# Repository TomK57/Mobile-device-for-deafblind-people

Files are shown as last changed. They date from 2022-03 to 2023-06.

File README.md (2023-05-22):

# Mobile-device-for-deafblind-people
(Eine Beschreibung der Markdown Formatierung für die Datei findet sich [hier](https://github.com/adam-p/markdown-here/wiki/Markdown-Cheatsheet)
## Motivation
The biggest problem for deafblind people is social isolation.
Ofcourse they can read books printed in Braille or write a letter using a Braille keyboard, but this is not the same as talking with somebody.
## The aim of the project
is to provide a technical solution which allows deafblind people to talk with somebody as similar to a normal talk as possible. 
## The 5 bit code
 
## System requirements
The system shall allow for full duplex communication  
The system shall use the haptic capabilities of the human fingers  
There shall be one device to be used with one hand for sending the information  
There shall be a second device to be used with the other hand for receiving the information  
In buildings the communication link between devices shall use WLAN  
In the field the system shall use mobile  infrastructure like 4G and 5G.  
The devices shall use Bluetooth to connect to mobile phones as links to the mobile infrastructure      
Sender and receiver device shall be designed with best ergonomic properties in mind  
The sender device shall have 5 contacts, one for each finger  
The contacts shall provide haptic feedback when pressed  
The receiver device shall have 5 contacts, one for each finger  
The contacts shall provide a haptic feedback when an information is sent to that finger.  
The kind of haptic feedback shall allow for use over several quarters of an hour without leading to artifacts in the sensation of the fingers.   
## System architecture - Top Level
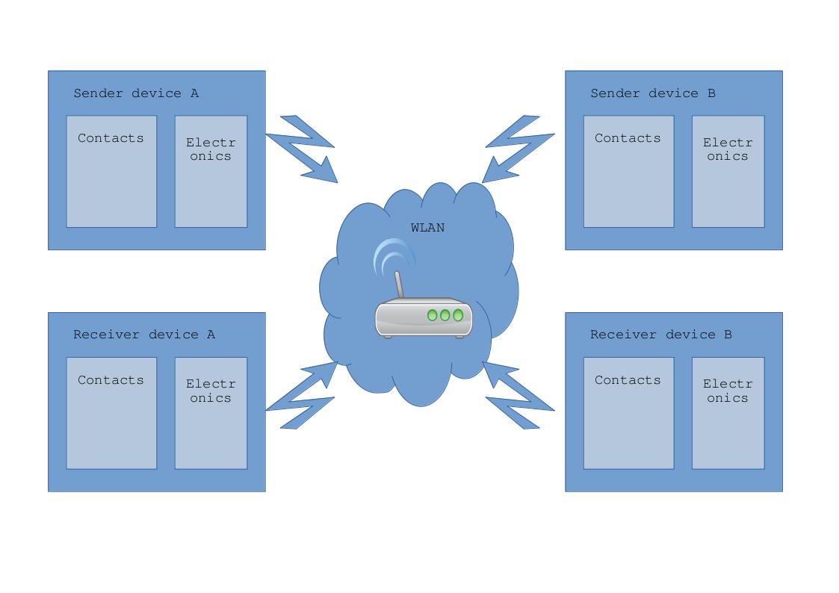
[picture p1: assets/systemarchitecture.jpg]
JPG image

### Power supply
The devices shall be able to operate from batteries (rechargeable).  
Battery lifetime tbd h (reasonable/acceptable)
### Performance
The devices shall be capable of processing at least 10 keystrokes per seconds   
## Pictures of some prototypes built so far
Evaluation of technical and ergonomic concepts<br><br>
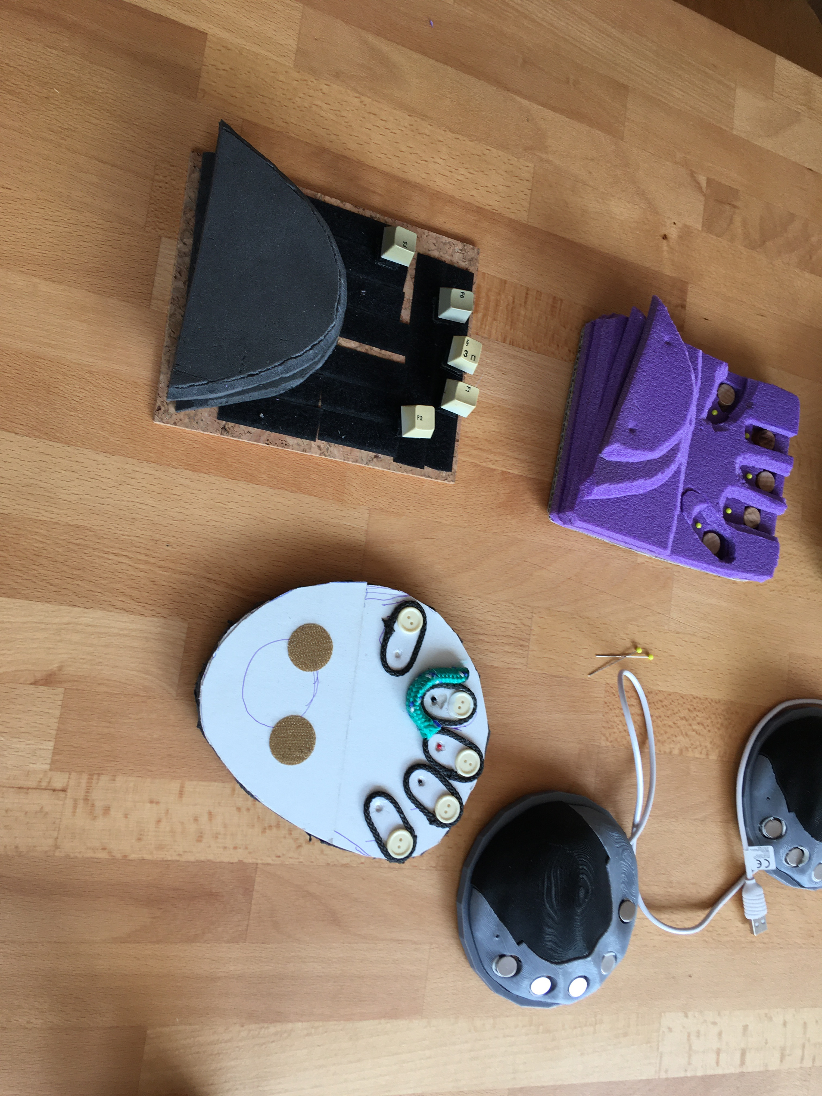
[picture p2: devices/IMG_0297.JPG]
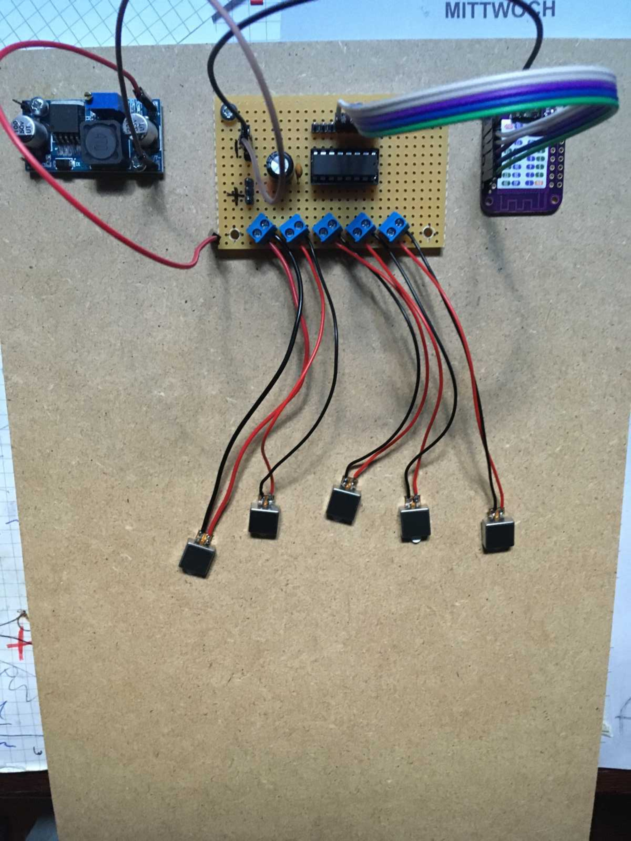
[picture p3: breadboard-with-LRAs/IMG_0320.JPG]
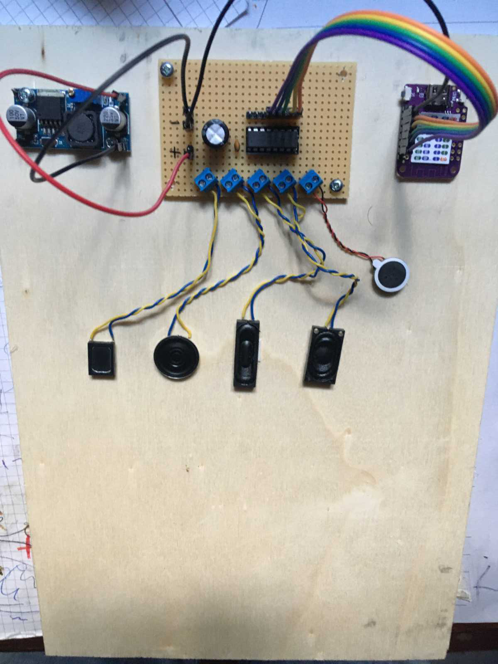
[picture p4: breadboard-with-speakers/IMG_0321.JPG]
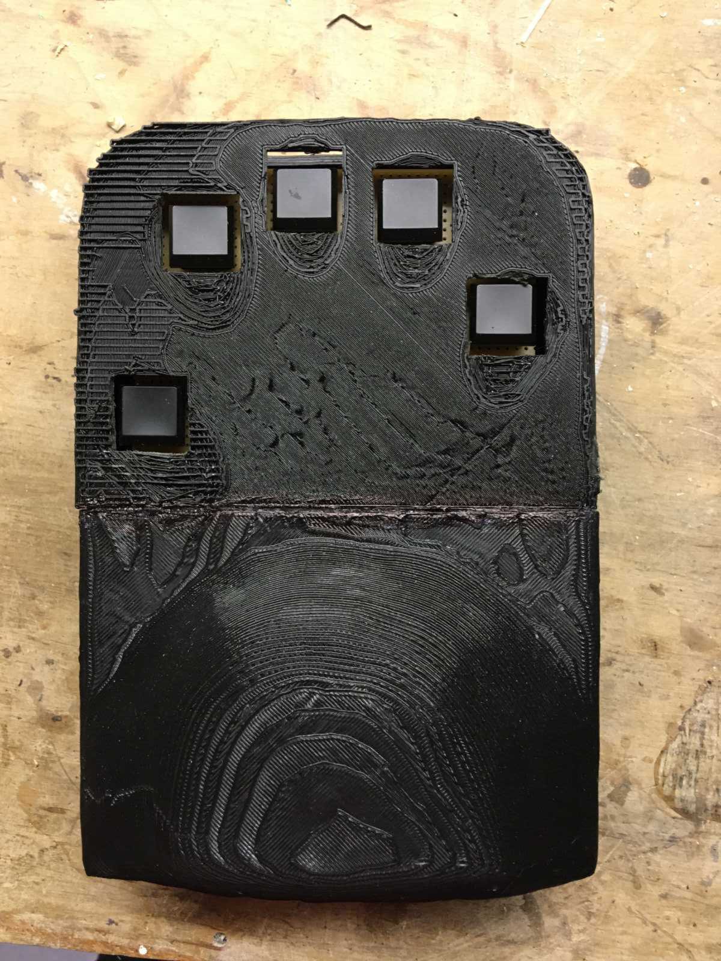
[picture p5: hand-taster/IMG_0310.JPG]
    <br>
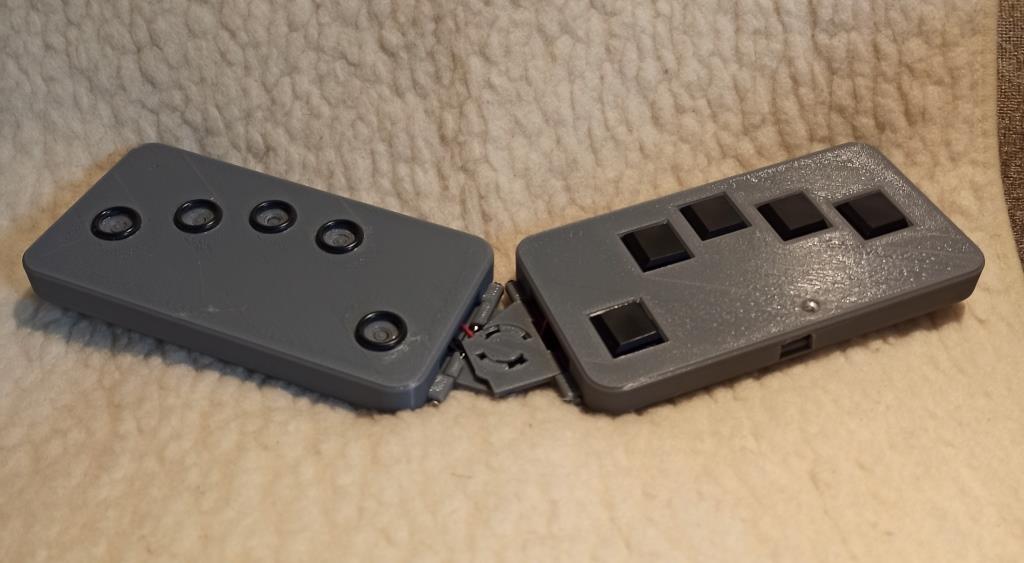
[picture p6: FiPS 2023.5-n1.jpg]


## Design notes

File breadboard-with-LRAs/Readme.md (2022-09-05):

## Breadboard with LRA's
LRAs are Loingitudinal Resonance Actuators, mostly used in mobiles. The model here is VLV101040A from vibronics.com.
This breadboard is used to test their usage for our purposes.
Electronics consist of WemosS2Mini controller, ULN2003 Darlington drver IC and a buck converter to provide the supply voltage for the LRAs independent from the controller.
The resonance frequecy of the LRA is 170Hz which means a period of about 5ms for one oscillation. We use only one half of this period to switch on voltage/current and let the device produce a mechanical pulse.
breadboard with LRAs
## software
to be used with hand taster device as input. ESP32_BLIND is basis for this modification.

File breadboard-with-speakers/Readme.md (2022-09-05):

## Breadboard with speakers
This device is intended to test the use of several speakers as actuators. Former tests showed that a user can feel the movement of the coil.
The electronics consist of Wemos S2 Mini (ESP32) controller, ULN2003 Darlington driver IC and a buck converter to provide the supply for the speakers indenpendent of the supply of the controller.
picture of breadboard
### Software
Works with the Handtaster device as input.

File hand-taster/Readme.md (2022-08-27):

## device for input with five low profile keys
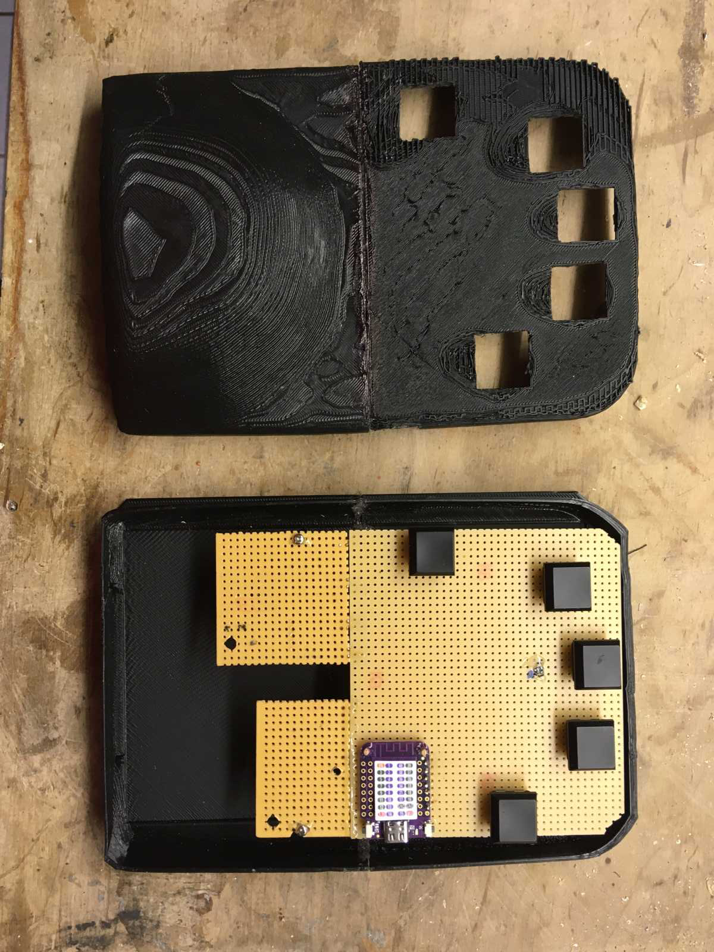
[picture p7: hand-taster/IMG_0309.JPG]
Bild1
<br>
Bild2<br>

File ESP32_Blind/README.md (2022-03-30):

DeafBlind Accesspoint / Websocket code with html webserver  for ESP32 or ESP8266                      copyright DHS, Desert Hard- & Software, Harald Wüst

See DB.docx Dokumentation...

Functionality:

The Sketch opens an acces point called "ap" with IP-adress 192.168.2.2.
A Web-Browser can access the startpage on this 192.168.2.2 or with http://dbserver.local

With the button "Socket communication" a socket connection to the device can be opened.

In the text field a single characters from the DeafBlind character set can be entered which is then send to the device and outputet to the DeafBlind tick-interface.

Also character entries made on the DeafBlind tick-interface are send to the web-socket console so that a communication with the DeafBlind can be established.

There are two special characters to extend the functionality:

- '#' This character switches to another character set (for example numbers, special characters). With each entry of a '#' character 
  the character set changes to the next one and back to the standard character set when the last set is reached (round robin).
  The following two character sets are currently available:
  'a','e','n','i','d','t','ä','o','k','m','f','l','g','ö','r','u','y','b','p','z','w','q','j','s','#','x','v','ü','c','h','*'  (standard set) and
  '1','2','3','4','5','6','7','8','9','0','!','"',' ','%','&','/','(',')','<','>',',','.','?',';','#','-','+',':','@','=','*'  (extended set)
  To destinguish the character sets on the DeafBlind tick-device for the first, normal set one pulse and for the second, third, ... sets two or more
  pulses are generated.
  After entering the next character from an extra character set the character set is automatically switched back to the standard character set.

- '*' This character switches to a special command mode. 
  In command mode the next entered character is interpreted as a special command:
  > '*' A second command character directly after the command character locks the comand mode permanently until another '*' character is recieved. This 
        can be used to enter a sequence of comands faster
  > 'w' Switch to local wifi network, the access point is closed and a connection to the local wifi network is established
  > 'c' Switch to client mode, the access point is colsed and a connection to another ap-server access point is opened to build up a network of devices.
  > 's' Switch to ap-server mode, the access point is opend to allow other devices to connect to the network of devices, only one server should be active.
  > 'n' Send new line/line feed character to begin a new input text line
  > 'm' Switch output mode, there are two output modes: 
        send all   -> sends every entered charcater including the special charcaters to all connected devices (standard mode after startup)
        send chars -> sends only the normal characters from the character set, special characters or commands are not send out 
        so that the output text is not disturbed
  > 'n' Send new line charater (cr/lf) to world
  > 'z' add space character ' ' to text line
  > 'e' Axecute previously stared text line (characters between the last new line commands. this can be used to process longer string comands also via
        tick-device (see description below). Example: * n s * z # 1 # 0 # 0 * n  command line "s 100" is stored, than * e to change stabTime
  > 'l' list alle connected devices with a given name to the world

All the single character input can come from the DeafBlind tick-device, the socket communication (other connected devices or web browsers) or the serial interface. So DeafBlind people can "talk" to each other or with non DeafBlinds using thier tick-devices.

If a longer string is entered via websocket or serial interface it is interpreted as a configuration command.
The first character of the command defines the functionality:

- 'o'   Send a string of characters to the network. Example "o hello" -> sends the character sequence  'h' 'e' 'l' 'l' 'o'  to the network 
        which is outputed to all connected DeafBlind tick devices.
- 's'   Set the stabilization time for character tick detection. Example s 20 -> sets the stabTime to 20 ms
- 'd'   Set the pulse duration for character tick output. Example d 20 -> sets the pulseDuration to 20 ms
- 'x'   Set the character speed for the 'o' command. Example x 200 -> sets the outSpeed to 200 ms
- 'n'   Change device name (wifi accesspoint and MDNS web browser name). Maximal length is 31 characters. Example n xy -> sets name to xy
- 'g'   Get (load) current configuration from file system. File ap.cfg is the startup configuration. Example g ap.cfg
- 'p'   Put (save) current configuration to file system. File ap.cfg is the startup configuration. File upload via web browser is possible. Example p ap.cfg
- 'i'   Change IP-Address, config save and reebot neccessary! (3.digit format with leading zerros) Example: i 192.168.002.002
- '!'   Special WebSocket command! Set name of connected device after new connection, to be send from client. Example: !xy -> sets device name to xy
- 'rrr' reeboot the tick-device

To start a DeafBlind network the devices should be startet one after the other giving them a uniqe name ('n MaxMusterman') and switch to client mode ('*' 'c'). Only the last device should stay in server mode where all other devices will than start to connect to.

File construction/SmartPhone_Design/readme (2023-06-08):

3D printing files for smartphone design Jun 2023

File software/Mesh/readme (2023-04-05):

DeafBlind SW for DeafBlind devices based on ESP32 S2 µC, PainlessMesh Mesh-Network and Arduino-IDE 2.01

Copyright Desert Hard- & Software dhs-web.de e-mail: dhs-mail.de

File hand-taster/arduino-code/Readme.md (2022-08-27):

## Arduino code for model with Wemos S2 mini controller

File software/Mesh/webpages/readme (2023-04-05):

Web-Pages for DeafBlind device

Copyright Desert Hard- und Software, dhs-web.de e-mail: dhs-mail@gmx.de

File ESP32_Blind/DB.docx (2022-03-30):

| DeafBlind Anleitung Software Version V0.5 ESP32 / ESP8266
| DHS Desert Hard- & Software Dr. Harald Wüst 30.03.2022

# DeafBlind Anleitung

Software Version V0.5 ESP32 / ESP8266

## 1. Aufbau eines Geräte-Netzwerks

Für ein Geräte-Netzwerk sind genau ein DeafBlind Server und mehrere Clients erforderlich.

Der DeafBlind Server stellt dazu einen WiFi Acces-Point mit dem Namen DBServer zur verfügung mit dem sich die Clients verbinden.

## 2. Tick Eingabe

Das Tick-Gerät dient der Eingabe einzelner Zeichen aus dem DeafBlind Zeichensatz sowie weiterer Befehle. Dazu müssen die Finger einer Hand die fünf Kontaktflächen des Gerätes im richtigen Muster berühren. Den Buchstaben ‚a‘ erhält man z.B. durch Berühren der ganz rechten Kontaktfläche (bei der rechten Hand unter dem Daumen). Für den Buchstaben ‚h‘ muss man die vier anderen Finger auf die jeweiligen Kontaktflächen legen. Dabei sollten die Finger möglichst gleichzeitig die Kontakte berühren (die Zeit bis zu der alle Finger in Position sein müssen kann eingestellt werden, siehe 1-Tick s-Befehl).

Eine solche Eingabe eines Zeichens wird im Folgenden als Tick bezeichnet.

Für die Eingabe weiterer Zeichen können die Finger entweder kurz vollständig abgehoben oder (bei gleichen Teilen des Musters) nur die zu ändernden Finger abgehoben bzw. aufgesetzt werden.

Die eingegebenen Zeichen werden an alle Teilnehmer des Netzwerkes gesendet und an allen Tick-Geräten als Vibration bzw. im Web-Browser oder dem seriellen Interface ausgegeben (wenn aktiviert wird das Zeichen auch auf dem eigenen Tick-Gerät als aktive Rückmeldung ausgegeben
Hinweis: Abschaltung aktuell noch nicht implementiert)

Die Kontaktflächen werden von links nach rechts im Weiteren so benannt:

D (aumen),
Z (eigefinger),
M (ittelfinger),
R (ingfinger),
K (leiner Finger)

Abgehobene Finger werden durch einen Striche -- gekennzeichnet.

Das Zeichen ‚h‘ vom obigen Beispiel entspricht damit dem Tick

-- Z M R K -> h

Werden alle Finger auf den Kontaktflächen aufgelegt wird kein Tick ausgelöst.

D Z M R K -> „zuhören“

Damit kann man der Unterhaltung „zuhören“ da alle Ticks der anderen Teilnehmer auf dem eigenen Tick-Gerät ausgegeben werden.

Hinweis: Da alle Eingaben direkt an alle Teilnehmer weiter gegeben werden kann es bei einer größeren Anzahl Teilnehmer schnell zu durcheinander kommen. Dies ist identisch mit dem durcheinander reden bei einer sprachlichen Unterhaltung und kann durch Disziplin der Teilnehmer reduziert werden.
Es kann auch auf den Rais-Hand Modus umgeschaltet werden in dem der DeafBlind Server die Rederechte verwaltet und immer nur ein Benutzer aktiv geschaltet ist. Die anderen Benutzer müssen zuerst das Rederecht durch ein „Handheben“ anfordern. Der Server fordert dann jeweils den nächsten Benutzer durch Ausgabe des Geräte-/Nutzer-Namens zum „reden“ auf.

Der RaiseHand Modus ist aktuell noch nicht vollständig Implementiert!

## 2.1. Zeichensätze

Der Standard-Zeichensatz ist folgender:

a D -- -- -- --
b -- Z -- -- K
c D – M R K
d D – M -- --
e -- Z -- -- --
f D Z -- -- --
g D – M R --
h -- Z M R K
i -- -- M -- --
j D Z M – K
k D -- -- R --
l -- -- M R --
m -- Z – R --
n D Z -- -- --
o -- -- -- R --
p D Z -- -- --
q -- Z M -- --
r D Z M R --
s -- -- -- R K
t -- Z M -- --
u -- -- -- -- K
v D Z -- R K
w D -- M -- K
x -- Z -- R K
y D -- -- -- K
z -- -- M – K
ä D Z M -- --
ö -- Z M R --

Über den speziellen Tick „Zeichensatzwechsel“ (im Weiteren als # bezeichnet):

# D -- -- R K

kann auf weitere Zeichensätze umgeschaltet werden:

1 2 3 4 5 6 7 8 …

A B C D E F G …

Dabei wird mit jedem Zeichensatzwechsel-Tick zwischen den Zeichensätzen im Kreis gewechselt. Da die Zeichenwechsel-Ticks ebenfalls an die anderen Teilnehmer übermittelt werden sind diese über den aktuell aktiven Zeichensatz informiert (abhängig vom Ausgabe-Modus, siehe m-Befehl).

Der neue Zeichensatz bleibt jeweils nur für das nächste Zeichen aktiv und wird dann wieder auf Normal zurück gesetzt.

Mit der Tick-Eingabe
# # h a l l o
bekommen Sie die Ausgabe
# # H a l l o
da durch zwei Mal # auf die Großbuchstaben umgeschaltet wurde.

Um die Umschaltung dauerhaft zu aktivieren (um z.B. eine längere Zahlenfolge einzugeben) muss nach der Wahl des Zeichensatzes der „Befehls-Zeichen“ Tick ‚*‘ gegeben werden (siehe Kap. 2):
# * a e n i
gibt die Ausgabe
# * 1 2 3 4

Mit dem nächsten Zeichensatz-Tick # wird wieder auf den Standard Zeichensatz zurück geschaltet.

Hinweis: Im Normal-Modus (siehe m-Befehl) kann eine zwischenzeitliche Tick-Eingabe eines anderen Teilnehmers die Umschaltung auf den dritten Zeichensatz und/oder die dauerhafte Aktivierung des Zeichensatzes stören (da dazu 2 direkt aufeinander folgende Ticks erforderlich sind).

## 3. 1-Tick Befehle

Mit dem speziellen Tick „Befehls-Zeichen“ (im Weiteren als * bezeichnet)

* -- -- M R K

können sogenannte 1-Tick Befehle ausgeführt werden. Damit lassen sich diverse Funktionen des Gerätes einfach steuern wobei die anderen Teilnehmer über alle Steuer-Befehle durch die Befehls-Zeichen Sequenz informiert sind (abhängig vom Ausgabe-Modus, siehe m-Befehl).

Ein 1-Tick Befehl besteht immer aus dem *-Tick gefolgt von dem gewünschten 1-Tick Befehlszeichen.

Hinweis: Im Normal-Modus (siehe m-Befehl) kann eine zwischenzeitliche Tick-Eingabe eines anderen Teilnehmers die Befehlsausführung stören oder zur Aktivierung eines falschen Befehls führen (da dazu 2 direkt aufeinander folgende Ticks erforderlich sind).

Eine mögliche Verbesserung durch Blockieren anderer Eingaben für eine gewisse Zeit und Rücknahme des Befehl-Ticks ist aktuell noch nicht umgesetzt!

Es gibt folgende 1-Tick Befehlszeichen / Funktionen:

## 3.1. w

Umschalten auf WLan Verbindung
Hinweis: aktuell feste Netzwerkdaten, Problem mit EEPROM-Lib auf ArduinoDroid!

## 3.2. c

Umschalten auf Client-Modus.
Es wird für 10 Sekunden versucht eine Verbindung zum DeafBlind Server (Access-Point DBServer) herzustellen und dem DeafBlind Netzwerk beizutreten. Wenn die Verbindung aufgebaut werden konnte wird der Name des Geräts/Benutzers an den Server übertragen (siehe n-Befehl). Andernfalls wird auf den Acces-Point Server Modus zurück geschaltet.

## 3.3. s

Umschalten auf Acces-Point Server Modus. Das Gerät stellt den DeafBlind-Server (DBServer) Access-Point zum Verbinden weitere Geräte im DeafBlind-Netzwerk zur Verfügung.

## 3.4. m

Ändern des Ausgabe-Modus. Im Standard Ausgabe-Modus (0) werden alle Zeichen incl. Befehlszeichen ausgegeben. Im Reduzierten Modus (1) werden die Befehlszeichen unterdrückt damit die Text-Ausgabe nicht gestört wird. Dieser Modus kann zum Schreiben von Texten benutzt werden.
Hinweis: Im reduzierten Modus sehen andere Teilnehmer die Befehlseingaben nicht und kennen daher Änderungen an der Systemkonfiguration nicht mehr.

Im Raise-Hand Modus (siehe r-Befehl) werden alle Ausgaben unterdrückt bis der Server die Raise-Hand Anfrage des Gerätes/Benutzers akzeptiert hat. Damit kann sicher gestellt werden, dass nicht mehrere Nutzer gleichzeitig kommunizieren.
Hinweis: Aktuell ist dieser Modus nicht vollständig implementiert.

## 3.5. r

Ein- / Ausschalten des Raise-Hand Modus.
Hinweis: Aktuell ist dieser Modus nicht vollständig implementiert.

## 3.6. h

Raise-Hand, Kommunikationsfreigabe beim Server anfordern

Hinweis: Aktuell ist dieser Modus nicht vollständig implementiert.

## 3.7. n

Sende „Return“ (Zeilenrücklauf / neue Zeile) an die verbundenen Geräte. Die seit dem letzten Zeilenwechsel gesendeten Zeichen werden in einem Zeilen-Speicher für die weitere Verwendung zwischengespeichert (siehe e-Befehl).

Es wird kein Zeichen an die Tick-Geräte gesende.

## 3.8. z

Sende „ “ (Leerzeichen) an die verbundenen Geräte. Das Leerzeichen wird nicht an den Tick-Geräte als Tick sondern nur als kurze Pause ausgegeben (siehe o-Befehl).

## 3.9. e

Ausführen einer gespeicherten Zeile (siehe n-Befehl). Über diese Funktion können auch Zeilen-Befehle (siehe Kap. 3) über ein Tick-Gerät ausgeführt werden indem zuerst eine neue leere Zeile über den n-Befehl gestartet wird, dann der gewünschte Zeilen-Befehl mit dem Tick-Gerät geschrieben und die Zeile mit einem weiteren n-Befehl abgeschlossen wird.

Der Zeilen-Befehl ist damit in den Zeilen-Speicher übertragen und kann als Ganzes über den e-Befehl ausgeführt werden.

## 3.10. l

Auflisten aller im Netzwerk verbundener Geräte. Es werden nacheinander die Gerätenamen ausgegeben, so dass die Nutzer eine Übersicht bekommen wer an der Unterhaltung gerade teilnimmt.

Hinweis: Beim Web-Zugang muss der Name mit einer Zeilen-Befehlseingabe ! Gerätename (siehe n-Befehl) selbst gesetzt werden. Andernfalls wird der Zugang als „unknown“ ausgegeben.

## 4. Zeilen Befehle

Befehls-/Text-Eingaben mit mehr als einem Zeichen (diese können über das Serielle Interface oder die Web- Verbindung direkt eingegeben werden) werden als Zeilen-Befehle interpretiert.

Folgende Funktionen stehen dabei zur Verfügung (jeweils Angabe einer Beispiel Befehlszeile):

## 4.1. s 100

Ändern der 1-Tick Stabilisierungszeit in Millisekunden. Die angegebene Zeit bestimmt wie schnell einzelne Zeichen über das Tick-Gerät eingegeben werden können (Zeit von der ersten Berührung einer Sensorfläche bis zum Setzen aller Finger). Hohe Werte ermöglichen eine sichere Bedienung, niedrige Werte ein schnelleres Schreiben. Die Werte sollten zwischen 50 (max. 10 Zeichen/s) und 250ms (max. 2 Zeichen/s) liegen.
Hinweis: Die Zeit wird in der Konfiguration gespeichert (siehe p-Befehl).

## 4.2. d 5

Ändern der Tick Pulse-Dauer in Millisekunden. Die angegebene Zeit bestimmt wie lange ein Zeichen über das Tick-Gerät ausgegeben wird (Dauer der Vibration). Hohe Werte ermöglichen eine sichere Erkennung, niedrige Werte ein reduzierten Fingerreitz. Die Werte sollten zwischen 5 und 100ms liegen.
Hinweis: Die Zeit wird in der Konfiguration gespeichert (siehe p-Befehl).

## 4.3. x 500

Ändern der Ausgabegeschwindigkeit der Zeichen einer Textzeilen in Millisekunden. Die angegebene Zeit bestimmt wie schnell hintereinander die einzelnen Zeichen bei der automatischen Ausgabe einer längeren Textzeile aufeinander folgen. Hohe Werte ermöglichen eine sichere Erkennung, niedrige Werte ein schnelleres Lesen. Die Werte sollten zwischen 5 (100 Zeichen/s) und 1000ms (1 Zeichen/s) liegen.
Hinweis: Die Zeit wird in der Konfiguration gespeichert (siehe p-Befehl).

## 4.4. o text

Automatische Ausgabe des angegebenen Textes an alle verbundenen Geräte. Die Ausgabe erfolgt mit der eingestellten Geschwindigkeit (siehe x-Befehl) als käme sie von einem Tick-Gerät (alle enthaltenen Befehls-Zeichen (siehe 1-Tick Befehle) werden ausgeführt).

## 4.5. n name

Ändern des Gerätenamens. Der Gerätename wird zur Identifizierung des Gerätes/Benutzers im Gerätenetzwerk verwendet. Die Zeichen des Namens müssen aus dem Standard Zeichensatz sein da sie bei Bedarf über das Tick-Gerät ausgegeben werden (siehe l-Befehl). Es sollten daher kurze, eindeutige Namen bzw. Initialen verwendet werden.

Hinweis: Der Name wird in der Konfiguration gespeichert (siehe p-Befehl).

## 4.6. r r

Reboot des Gerätes. Alle Einstellungen werden auf die in ap.cfg gespeicherte Konfiguration zurückgesetzt (siehe p-Befehl) und die Netzwerkverbindung neu aufgebaut.

## 4.7. g ap.cfg

Die Konfiguration mit dem angegebenen Namen wird geladen.
Hinweis: Änderung der IP-Adresse und des Gerätenamens werden aktuell nicht aktiviert.

## 4.8. p ap.cfg

Die aktuele Konfiguration wird unter dem angegebenen Namen gespeichert. Die Konfiguration mit dem Namen ap.cfg wird bei jedem Start des Gerätes als Standard-Konfiguration geladen die daher hiermit geändert werden kann.

## 4.9. i 192.168.002.002

Ändern der Geräte-IP Adresse.
Die Zahlen müssen 3-Stellig eingegeben werden.
Hinweis: Damit die Änderung wirksam wird muss aktuell die neue Konfiguration unter ap.cfg gespeichert werden (siehe p-Befehl) und ein Reboot durchgeführt werden (siehe r-Befehl).

## 4.10. c ! 43

Ändern eines Zeichens in den Zeichensätzen. Als erstes wird das gewünschte Zeichen angegeben und danach die Position im Zeichensatz. Der erste Zeichensatz hat dabei die Positionen 0-31, der zweite Zeichensatz 32-63 und so weiter.
Hinweis: Die Zeichensätze müssen auf allen verbundenen Geräten gleich sein, Geräten die neu hinzu kommen bzw. nach einem Reboot sind die geänderten Zeichen nicht bekannt. Aktuell wird der Zeichensatz nicht in der Konfiguration gespeichert.

## 4.11. t 5

Tick-Modus einstellen. Das erste Bit im angegebenen Wert bestimmt, ob ein Tick erkannt und die Stabilisierungszeit (siehe s-Befehl) bei jeder Änderung gewartet wird (0) oder nur wenn Finger zusätzlich aufgesetzt werden (1). Damit kann nach einem kurzen Abheben einzelner Finger schneller ein neues Zeichen eingegeben werden, es können aber keine neuen Zeichen nur durch abheben von Fingern generiert werden.
Das zweite Bit gibt an, ob die Stabilisierungszeit ab der ersten Tick-Änderung unabhängig von weiteren Änderungen abläuft (schnelle Eingabe, nicht so robust bei nacheinander Setzen mehrere Finger) oder ob diese bei jeder Änderung innerhalb der Stabilisierungszeit neu beginnt (langsamer, robuster).

Hinweis: Der Tick-Modus wird aktuell in der Konfiguration nicht gespeichert.

## 4.12. q 15 04 18 22 23 32 33 34 35 25

IO-Ports einstellen. Die Portnummern müssen 2-Stellig in der Reihenfolge In0, In1, … In4, Out0, Out1, …, Out4 angegeben werden. Die Porteinstellung wird in der Konfiguration gespeichert (s. p-Befehl).

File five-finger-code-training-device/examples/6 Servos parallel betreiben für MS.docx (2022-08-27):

6 Servos parallel betreiben:

9V Batterien sind für Servos grundsätzlich zu schwach.

Vier Akkus in Größe AA reichen gerade eben für einen normalen oder zwei

mini Servos aus.

Du musst die Stromaufnahme aller Servos zusammen addieren, die

gleichzeitig aktiv sein könnten. Mit aktiv meine ich, dass sie ihre

Position ändern oder aufgrund mechanischer Einflüsse dagegen halten -

auch dann brauchen sie Strom. Und bedenke, dass die Motoren beim

Anlaufen in den ersten Millisekunden 5x so viel Strom aufnehmen wie

danach.

Für 6 Servos brauchst du schon ein kraftvolles Netzteil. Da kommst du

mit 9V Batterien oder Handy-Netzteilen nicht weiter.

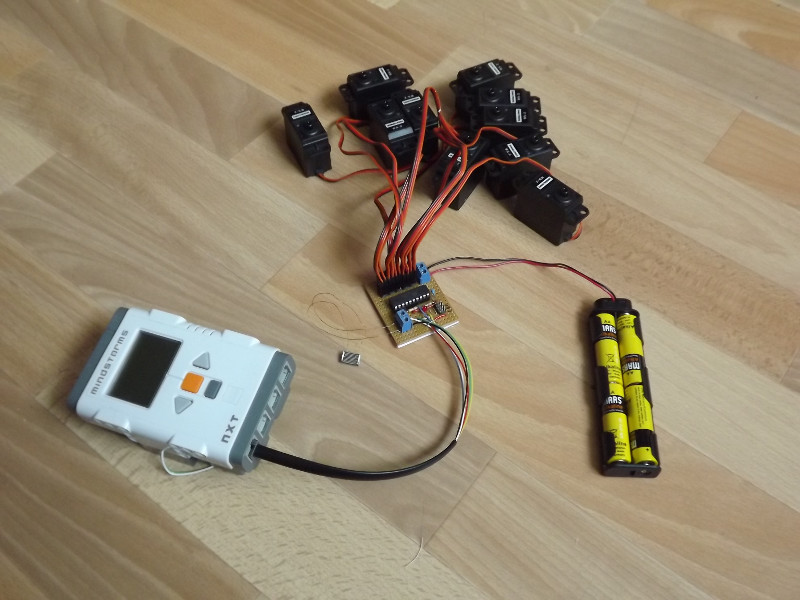
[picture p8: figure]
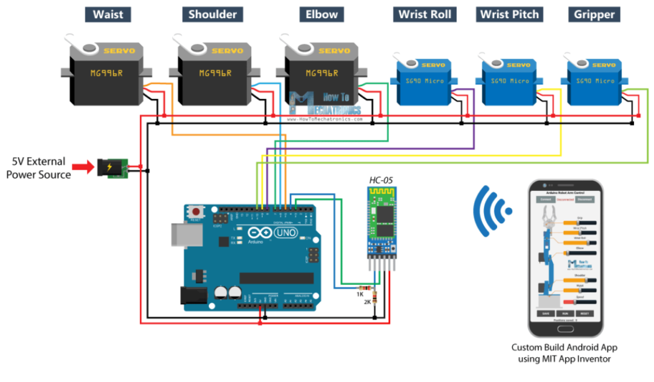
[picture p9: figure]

ttps://www.mikrocontroller.net/topic/474829

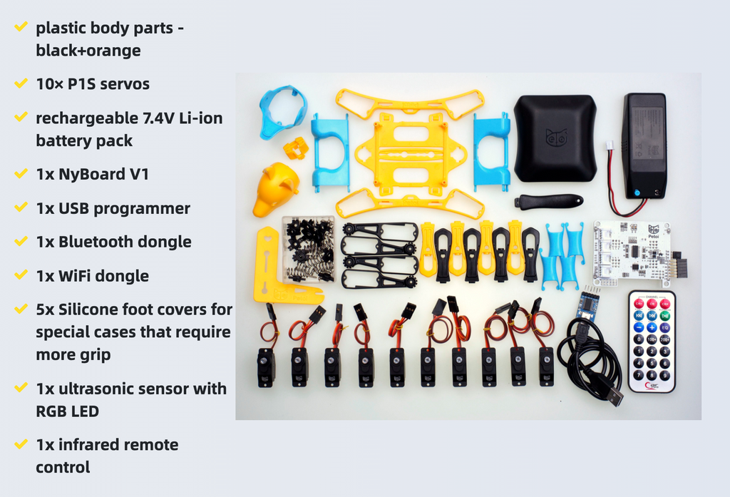
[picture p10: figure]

https://www.petoi.com/products/petoi-bittle-robot-dog?variant=40388667834552

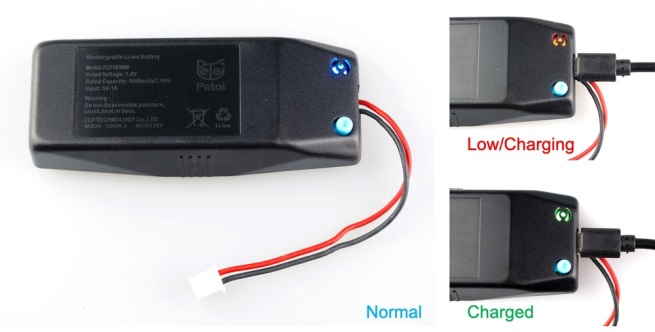
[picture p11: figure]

# Li-ion battery for Robot Dog Bittle (https://www.petoi.com/products/li-ion-battery-for-robot-dog-bittle)

$39.00

$36.00

A Li-ion battery pack to power robot dog Petoi Bittle for about one hour of continuous walking:

- can slide into the track underneath Bittle and tune its center of mass.
- has built-in charging and protection circuit, and an RGB LED to indicate the battery's status.
- with some reconfiguration, it can also power our previous Nybble models.

#### Specifications

- Output: 7.4V-5A (8.4V when fully charged)
- Capacity: 1000mAh/7.4Wh
- Input: 5V-1A
- Charging cable: micro-USB to USB
- Charger connector: regular USB charger (not included)
- Dimensions: 120mm x 60mm x 25mm (4.72 x 2.36 x 0.98 inch)
- Weight: 65g (2.3oz)

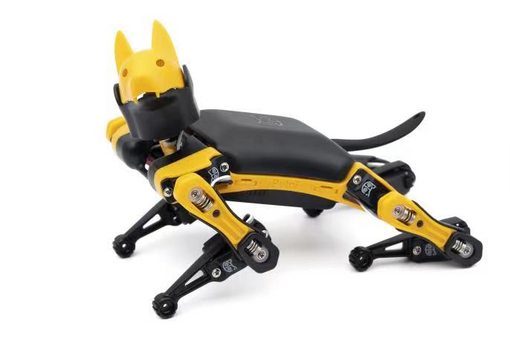
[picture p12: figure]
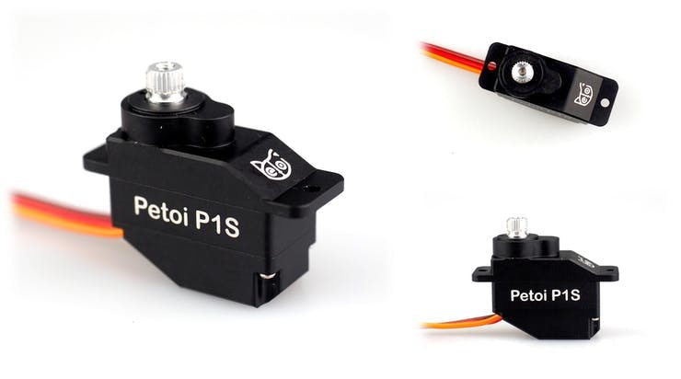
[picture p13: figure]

Aktuator

Traditionell werden kleine Servos für die Lenkung oder andere leichte Funktionen verwendet. OpenCat wurde populär, weil es das Potenzial der Servos für Hochleistungsbewegungen mit Beinen zeigte. Allerdings stellt der neue Anwendungsfall besondere Anforderungen an Geschwindigkeit, Drehmoment und Präzision. Die meisten Servos auf dem Markt sind nicht für Beinbewegungen optimiert. Nach unserer Rückkehr nach China haben wir mehrere Servohersteller besucht und viele Male wiederholt, um die besten Parameter zu finden. Wir haben das Modell mit OEM-Ausstattung versehen und nennen es Modell P1S mit kernlosem Motor, Alu-Getriebe, Kugellager und Kunststoffgehäuse. Es ist mit 8,4 V kompatibel, hat eine hohe Geschwindigkeit und einen steuerbaren Bereich von 270 Grad.

107 Projekte mit Arduinos

https://create.arduino.cc/projecthub/projects/tags/servo

Servo mit Joystick steuern

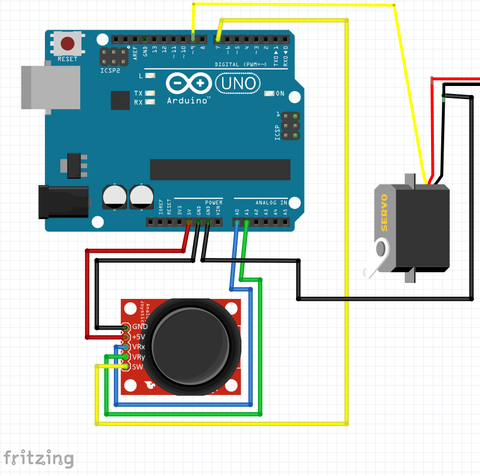
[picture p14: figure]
Schaltung

Wir helfen Ihnen

- FAQ & Hilfe (https://www.az-delivery.de/pages/faq-hilfe)
- Fragen zur Bestellung (https://www.az-delivery.de/pages/fragen-zur-bestellung)
- Technische Fragen (https://www.az-delivery.de/pages/technische-fragen)
- B2B Anfragen (https://www.az-delivery.de/pages/b2b-anfragen)
- Schulen und Universitäten (https://www.az-delivery.de/pages/schulen-und-universitaten)
- Telefon: 0991/99927827 (https://www.az-delivery.de/pages/about-us)
- info@az-delivery.com

Impressum

AZ-Delivery Vertriebs GmbH

Lärchenstraße 10

94469 Deggendorf Telefon: 0991/99927827

Montag-Freitag 10:00 - 16:00 Uhr 0,14€ / Min. inkl. MwSt. aus dem deutschen Festnetz, Mobilfunk max. 0,42€ / Min. inkl. MwSt.

E-Mail: info@az-delivery.com

Geschäftsführer: Malte Horeyseck

Im heutigen Blog Beitrag steuern wir einen AZ-Delivery Servo MG996R über eine Joystick Modul.

Dazu benötigen wir:

1x AZ-Delivery Servo MG996R

1x Joystick Modul

1x AZ-Delivery Mikrokontroller, kompatibel mit Arduino UNO R3

1x 3er Set 40 Stk. Jumper Wire m2m/f2m/f2f

Der Servo zieht im Betrieb bis zu 2,5A - viel zu viel für unseren Mikrokontroller, kompatibel mit Arduino Uno R3. Daher müssen wir Ihn über ein externes Netzteil versorgen.

Wir bauen unten stehende Schaltung auf. Dabei ist zu beachten dass wir GND vom Arduino mit dem GND des externen Netzteils verbinden.

Am Servo befinden sich 3 Leitungen. Die dunkelste (in unserem Fall Braun) ist GND. Rot ist wie fast immer VCC (4,8 - 7,2 V Stromaufnahme: bis 2,5A), und Orange wird vom Mikrokontroller, kompatibel mit Arduino Uno R3 gesteuert und mit Pin 9 verbunden.

Der Joystick hat 5 Anschlusspins welche wie folgt mit dem Mikrokontroller, kompatibel mit Arduino Uno R3 verbunden werden:

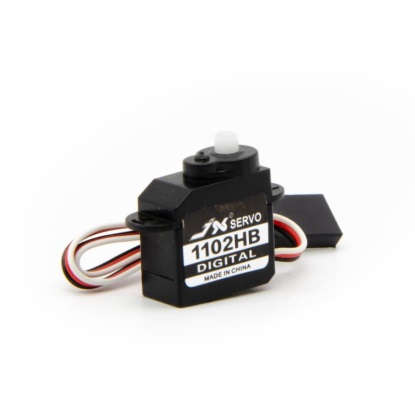
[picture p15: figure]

PDI-1102HB 2g Digital Micro Servo 0.26Kg*cm

Hersteller: JX-Servo, Artikelnr.: 421849, Verfügbarkeit: Lagernd, 9,50CHF

Technische Details:

Hersteller: JX-Servo

Hersteller SKU: PDI-1102HB

Eingangsspannung: 4.8V-5.5V

Geschwindigkeit bei 4.8V: 0.09s/60°

Geschwindigkeit bei 5.5V: 0.07s/60°

Drehmoment bei 4.8V: 0.24 kg*cm

Drehmoment bei 5.5V: 0.26 kg*cm

Dead band: 1 µs 1520 µs/330hz

Kabellänge 100mm

Max Drehwinkel: ca. 180°

Abmessung: 16.3 x 8.4 x 17.5

Gewicht Netto: 3.4g

Gewicht Brutto: 8.5g

Lieferumfang:

1x PDI-1102HB 2g Digital Micro Servo 0.26Kg*cm

1x Schraube für Servohebel

2x Befestigungsschrauben

3x Servohebel

Hackerspace Eastermundigen Bastelgarage.ch

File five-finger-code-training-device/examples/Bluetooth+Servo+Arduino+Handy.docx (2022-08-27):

Bluetooth-gesteuerter Servomotor mit Arduino, HC-05 Bluetooth-Modul

https://www.youtube.com/watch?v=rLIFpZhA-oQ

Bluetooth Controlled Servo Motor using Arduino, HC-05 Bluetooth Module

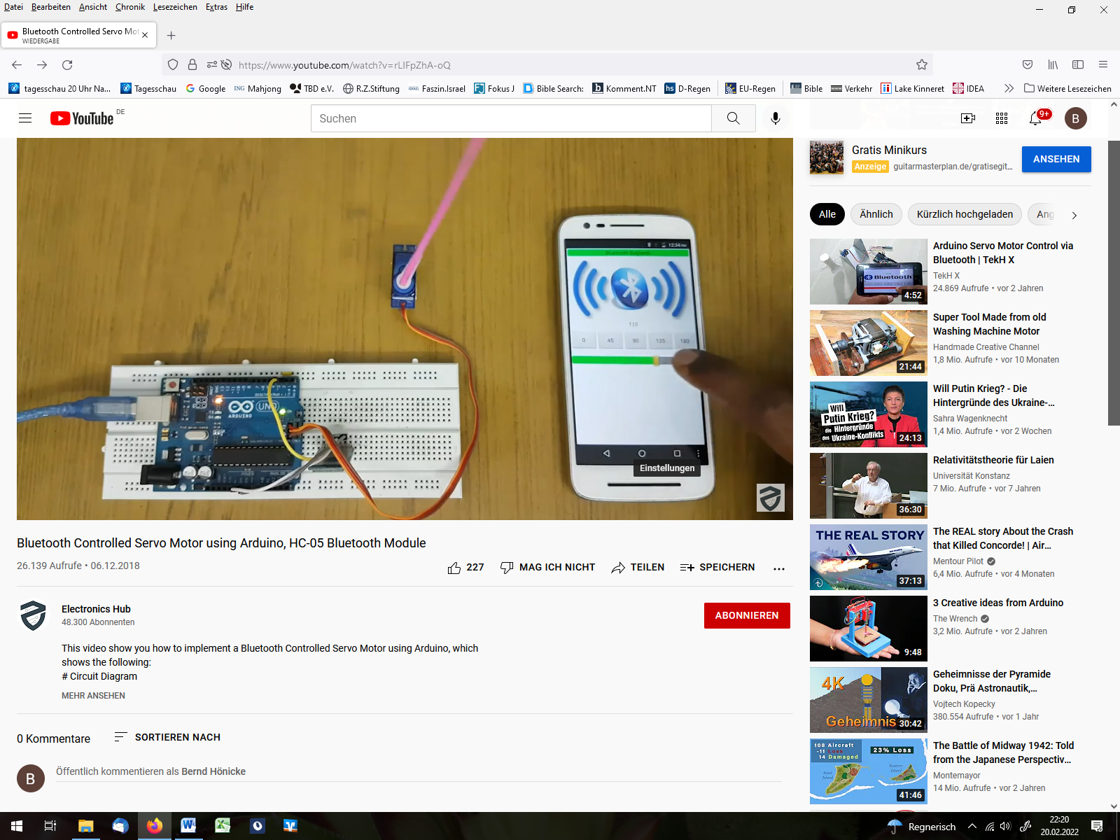
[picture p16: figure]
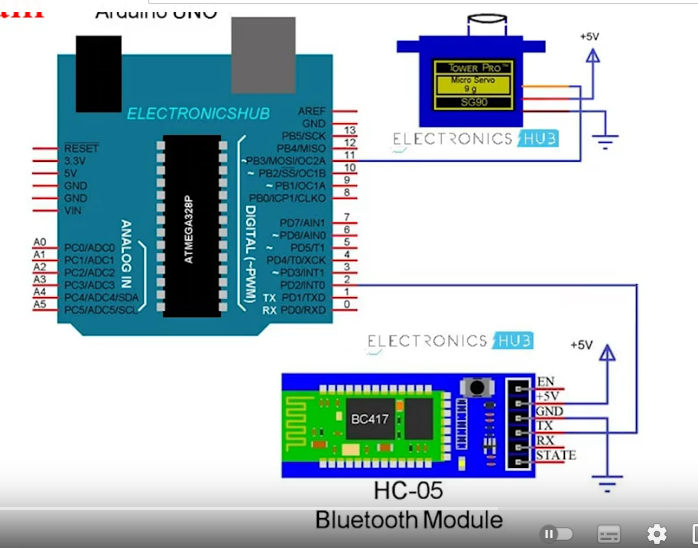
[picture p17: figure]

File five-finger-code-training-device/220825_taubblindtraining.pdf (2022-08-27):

Taubblinden Projekt - Trainigsgerät für Fünffinger Code

T. Kranz – 25.8.2022

Für die Kommunikation taubstummer Menschen soll ein Fünffinger Code eingeführt werden. Dieser Code muss erlernt werden. Dazu soll folgendes System dienen.
Mit dem Eingabegeräte A) können Buchstaben vorgegeben werden, die das Gerät B) mit taktilen Gebern wieder ausgibt. Die taktilen Informationen können von taubblinden Menschen mit den Fingern erfühlt werden.
Gerät A) und B) kommunizieren kabellos über eine Funkschnittstelle.
Gerät B) wird über ein externes Netzteil mit Strom versorgt.

Systemübersicht

Taktile Kontakte

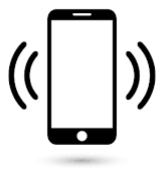
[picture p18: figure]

Die taktile Information soll mit Standard Servo-Motoren aus dem Bereich Modellbau umgesetzt werden.
Es werden je ein Servo-Motor für einen Finger verwendet.
z.B.

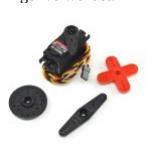
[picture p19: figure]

Skizze zu einer möglichen Ausführung auf der nächsten Seite ->

Empfänger B

Contacts Electr onics

### Supply

### Sender A)

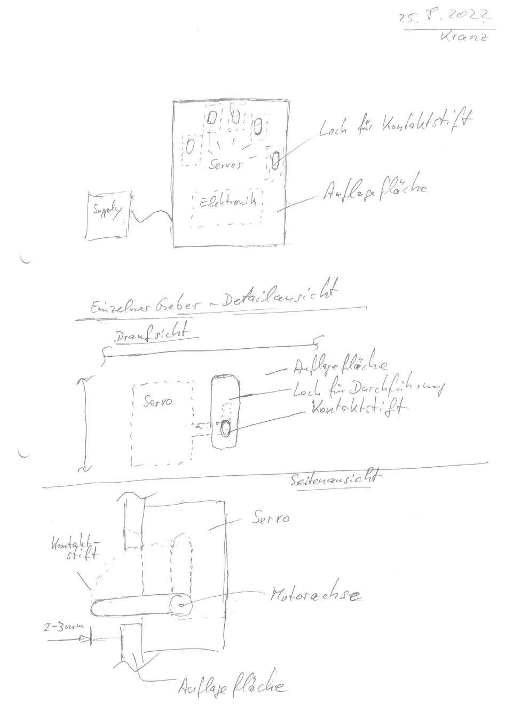
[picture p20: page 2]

Taubblinden Projekt - Trainigsgerät für Fünffinger Code

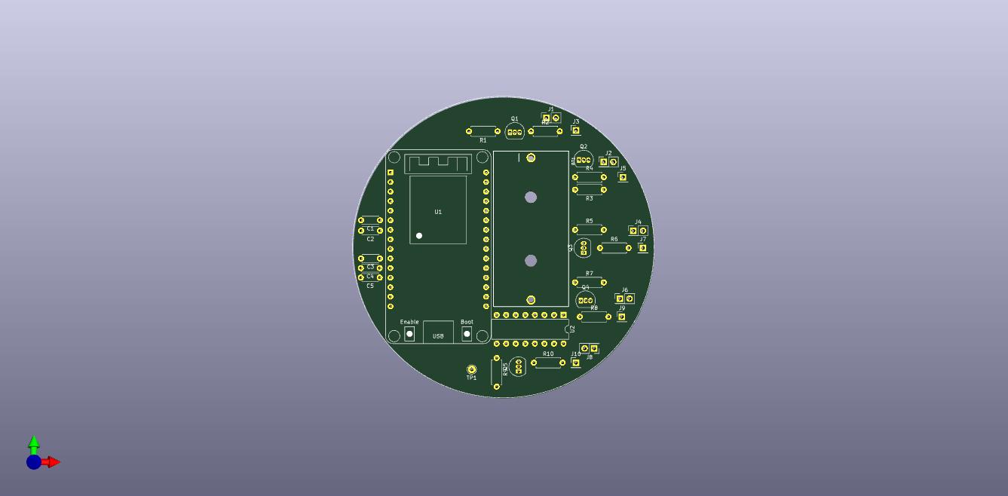
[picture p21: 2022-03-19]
hardware/220317_modb_pcb.jpg

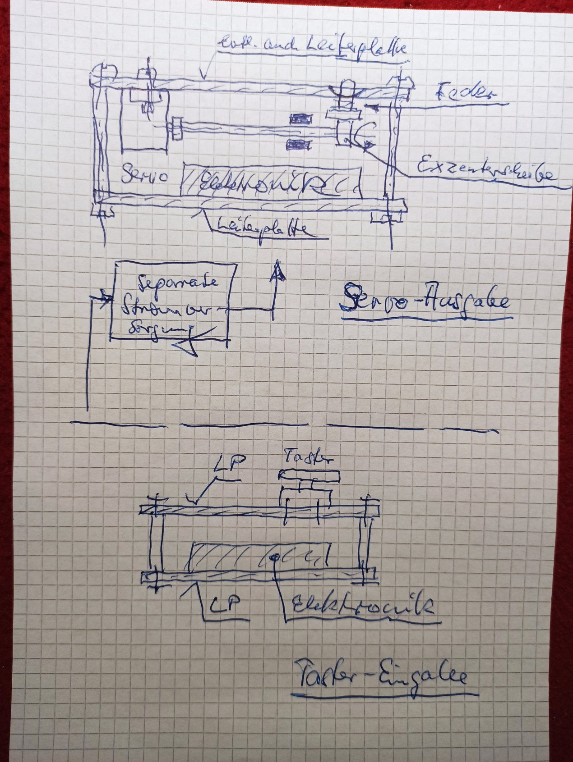
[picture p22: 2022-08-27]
five-finger-code-training-device/Skizze FiPS direktgekoppelt.jpg

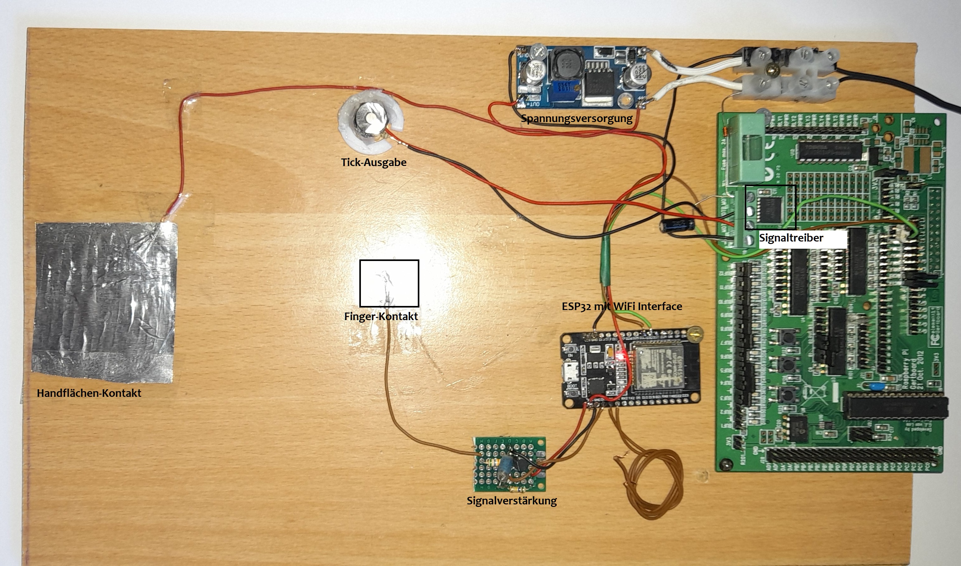
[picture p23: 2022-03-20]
ESP32_Blind/Prototyp.jpg

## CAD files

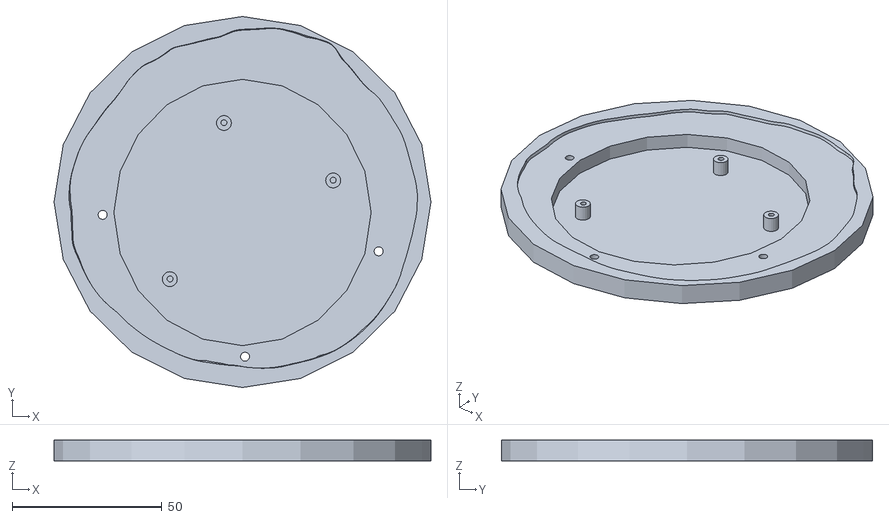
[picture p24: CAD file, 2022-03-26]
construction/3D/Boden.stl
126.0 x 124.0 x 7.00

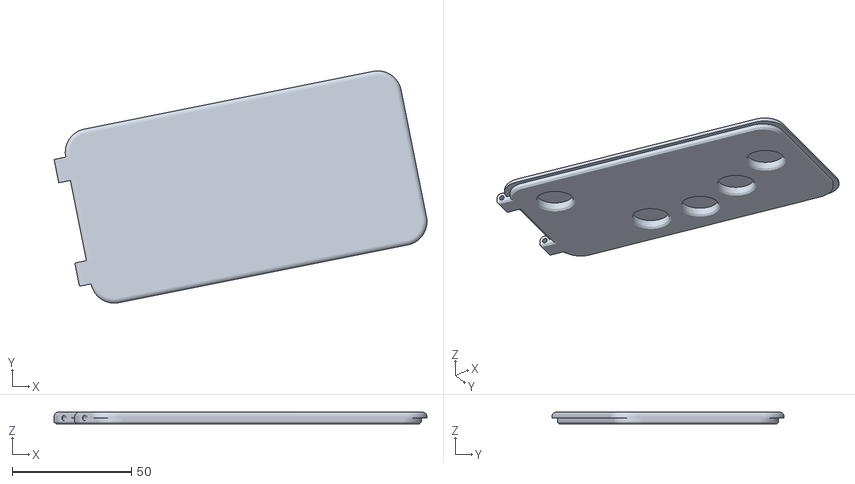
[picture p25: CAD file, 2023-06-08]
construction/SmartPhone_Design/Boden.stl
156.6 x 97.5 x 5.00

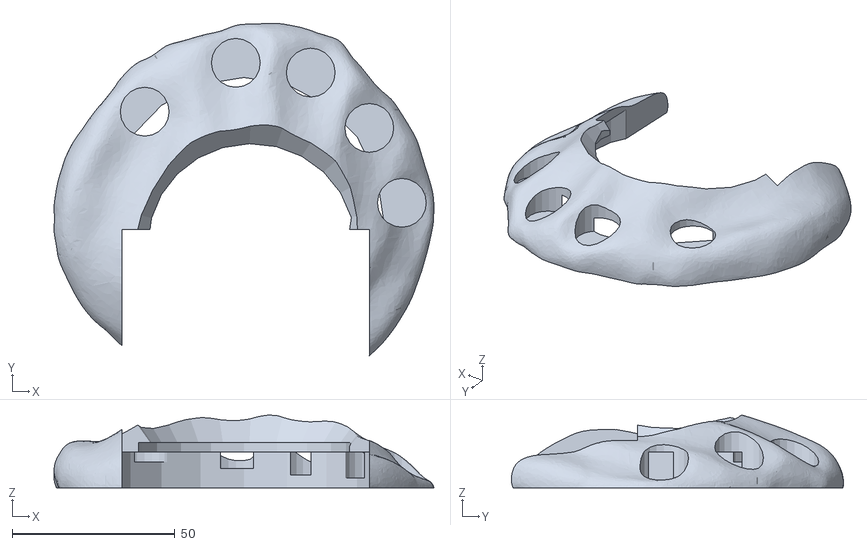
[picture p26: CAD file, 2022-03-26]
construction/3D/Deckel.stl
116.7 x 102.0 x 22.4

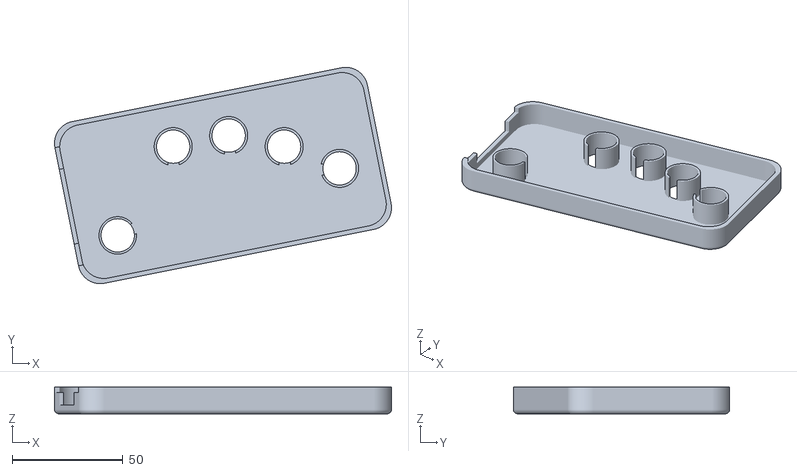
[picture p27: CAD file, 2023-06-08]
construction/SmartPhone_Design/Deckel.stl
151.9 x 97.5 x 12.0

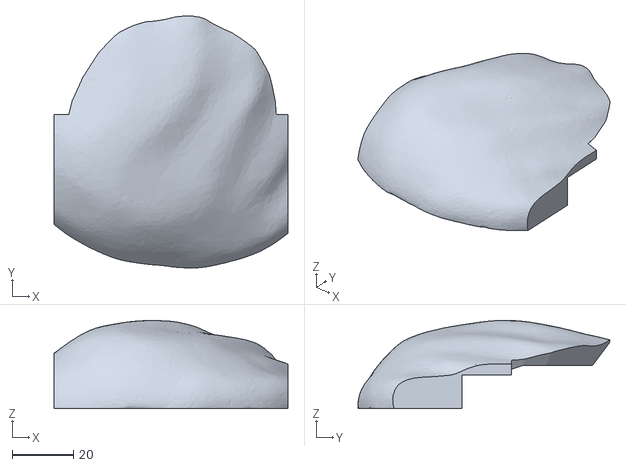
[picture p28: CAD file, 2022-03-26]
construction/3D/Deckel_Leitf.stl
76.0 x 82.0 x 28.7

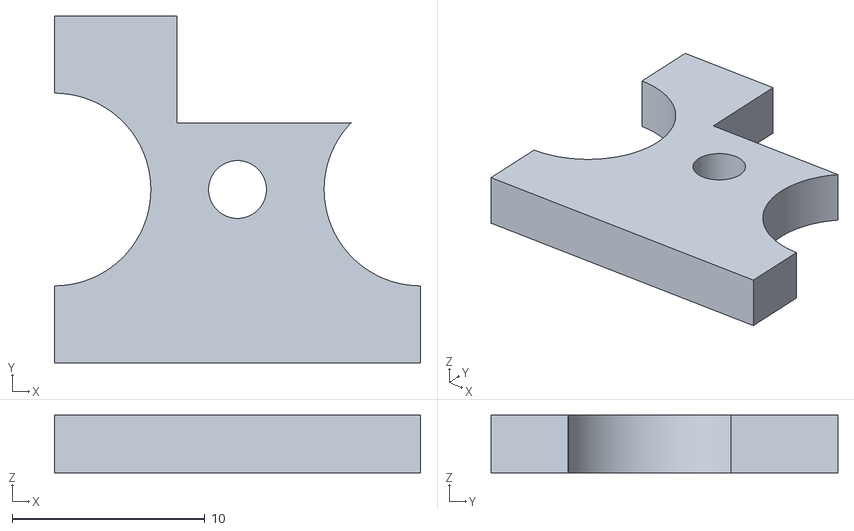
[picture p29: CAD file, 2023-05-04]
construction/SmartPhone_Design/T_Halter.stl
19.0 x 18.0 x 3.00

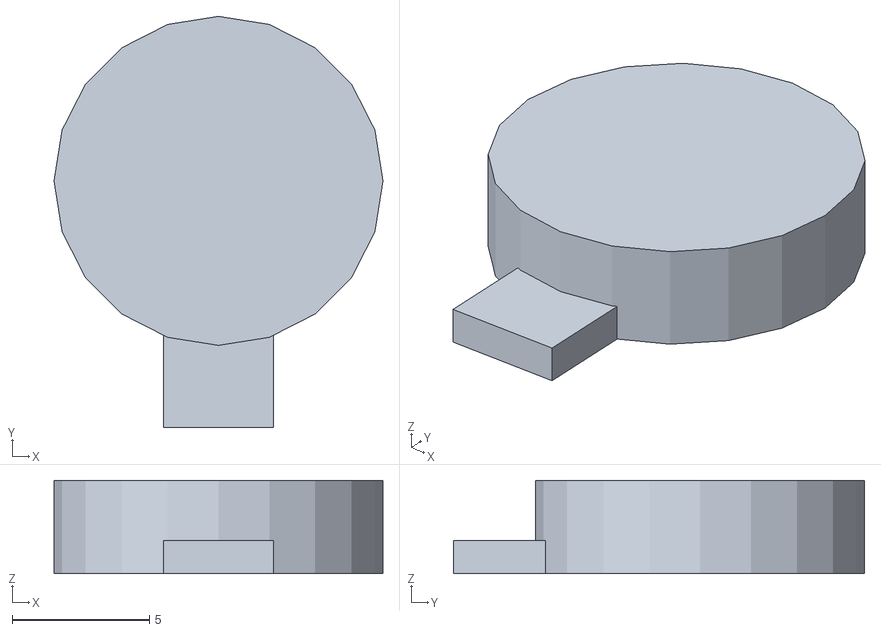
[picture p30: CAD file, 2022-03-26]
construction/3D/Motor.stl
12.0 x 15.0 x 3.40

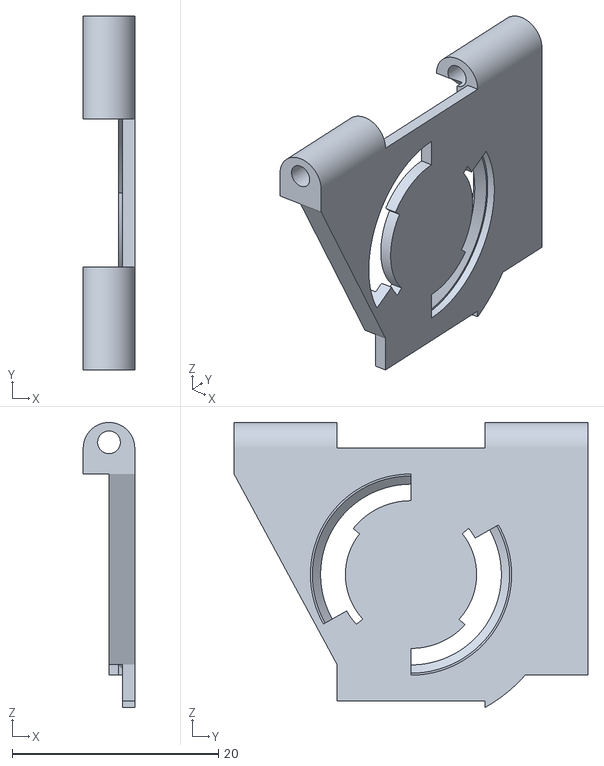
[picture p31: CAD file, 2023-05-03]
construction/SmartPhone_Design/H2.stl
5.00 x 34.3 x 27.6

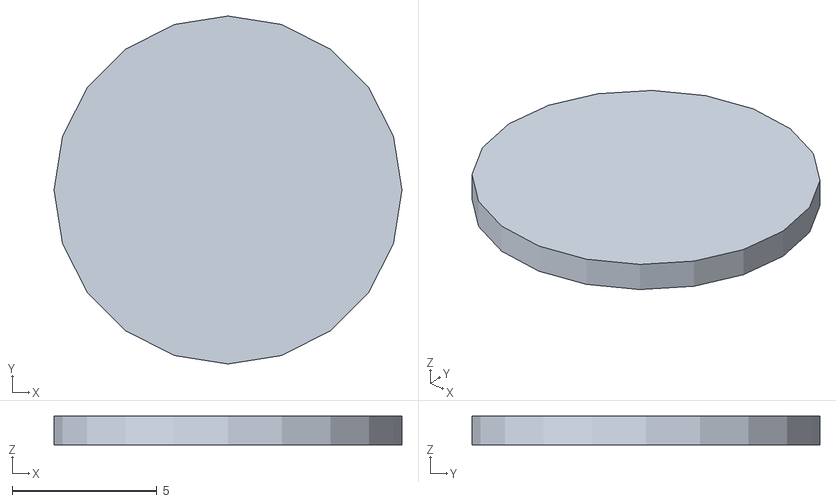
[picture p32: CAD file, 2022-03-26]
construction/3D/Scheibe_Leitf.stl
12.0 x 12.0 x 1.00

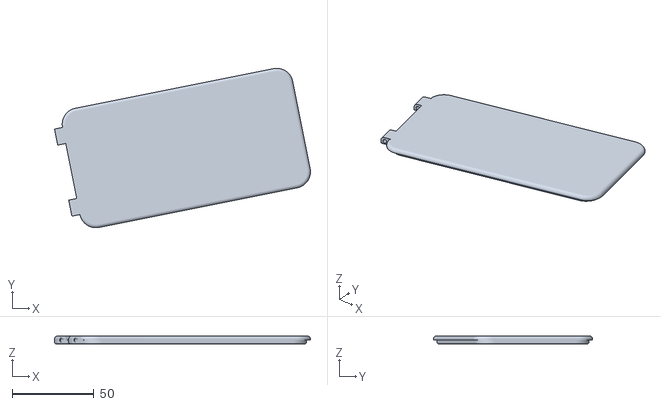
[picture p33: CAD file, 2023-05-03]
construction/SmartPhone_Design/Boden_tast.stl
156.6 x 97.5 x 5.00

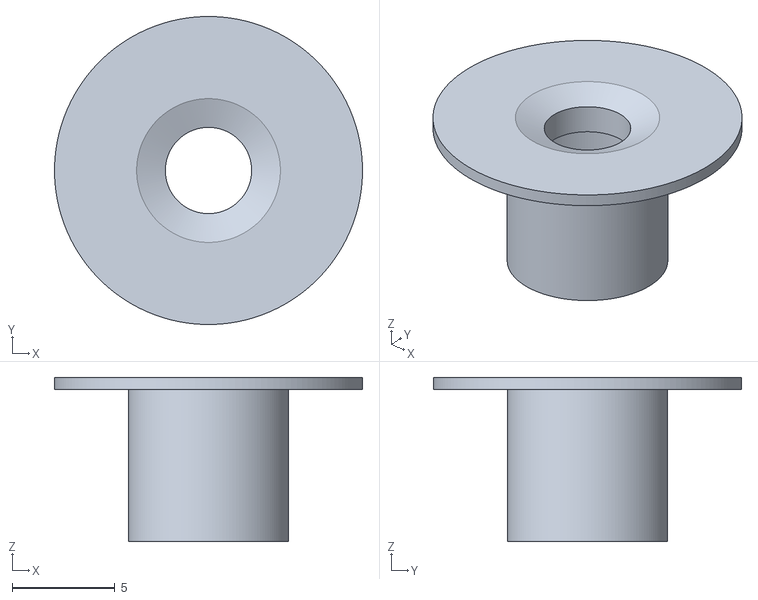
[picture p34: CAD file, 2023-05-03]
construction/SmartPhone_Design/SP_Halter1.stl
15.0 x 15.0 x 8.00

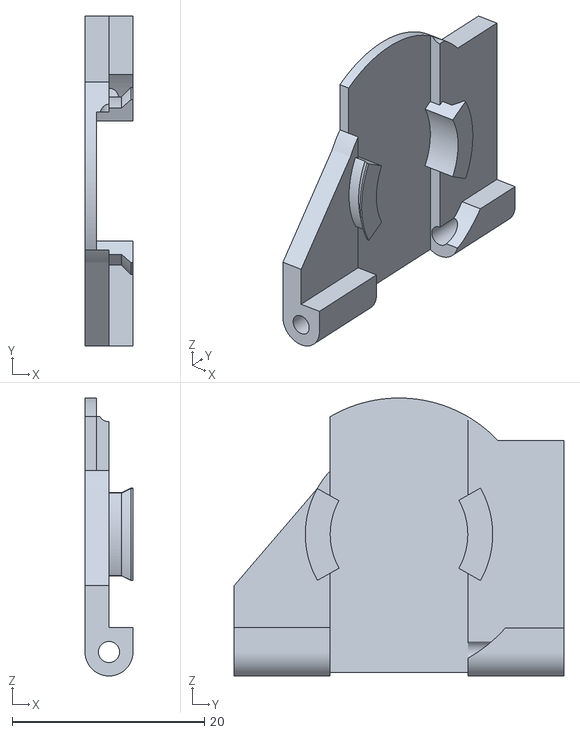
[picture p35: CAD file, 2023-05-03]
construction/SmartPhone_Design/H1.stl
5.00 x 34.3 x 28.9

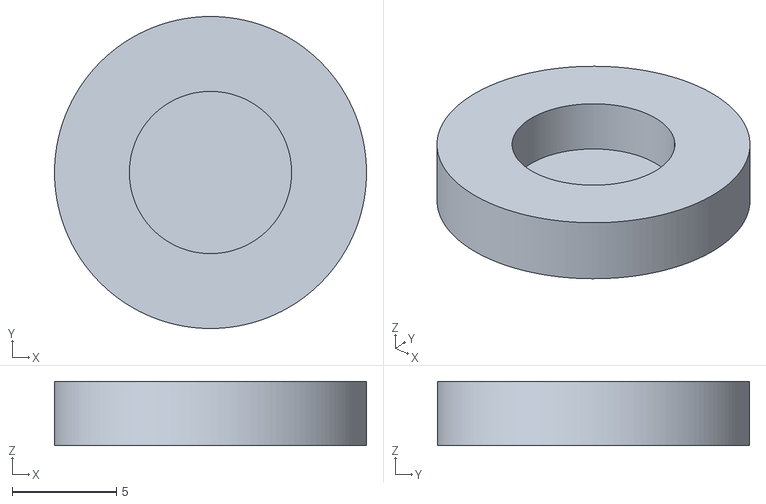
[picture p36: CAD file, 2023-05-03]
construction/SmartPhone_Design/SP_Halter2.stl
15.0 x 15.0 x 3.10

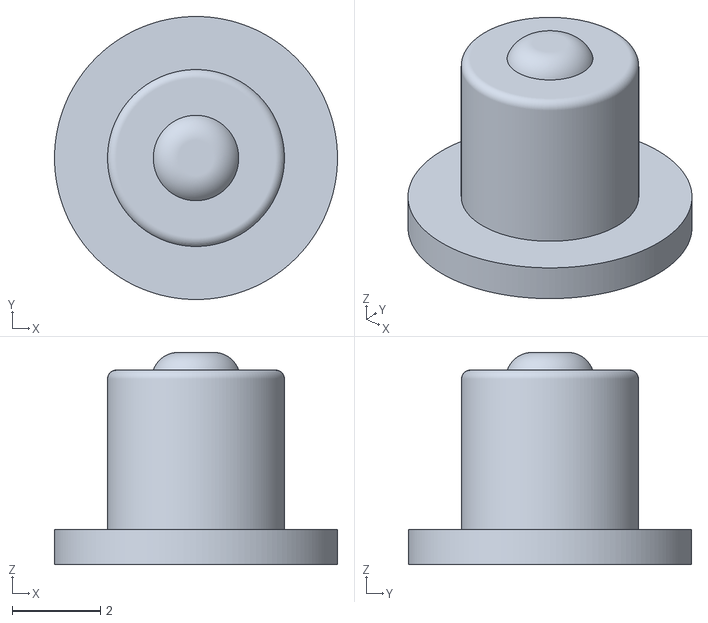
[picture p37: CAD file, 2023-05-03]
construction/SmartPhone_Design/Mag_Halter.stl
6.40 x 6.40 x 4.80

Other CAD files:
construction/SmartPhone_Design/Deckel_tast.stl
hardware/type3/220322_modp-220317_modb.step

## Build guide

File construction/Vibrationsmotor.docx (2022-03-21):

Vibrationsmotor

https://de.aliexpress.com/i/4000383426740.html

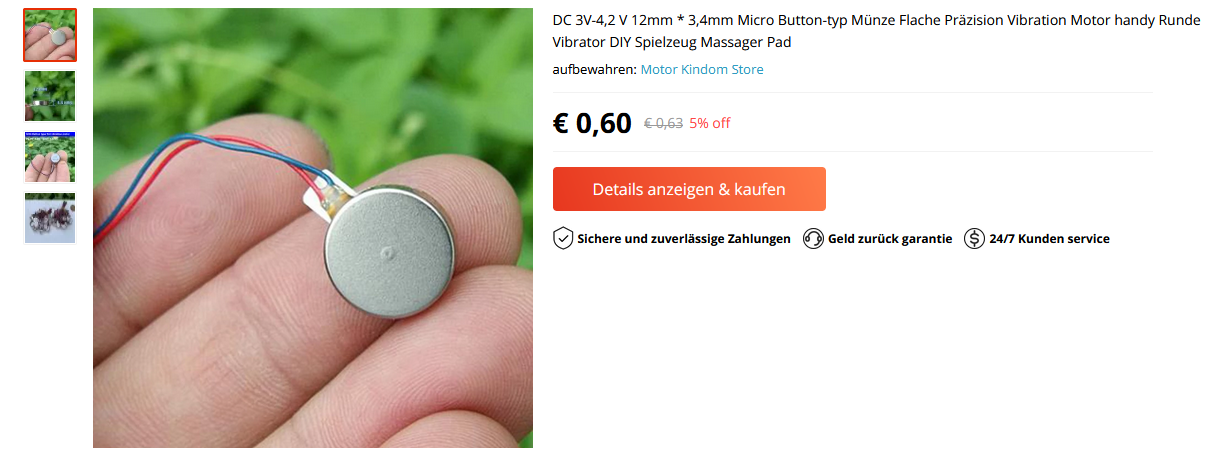
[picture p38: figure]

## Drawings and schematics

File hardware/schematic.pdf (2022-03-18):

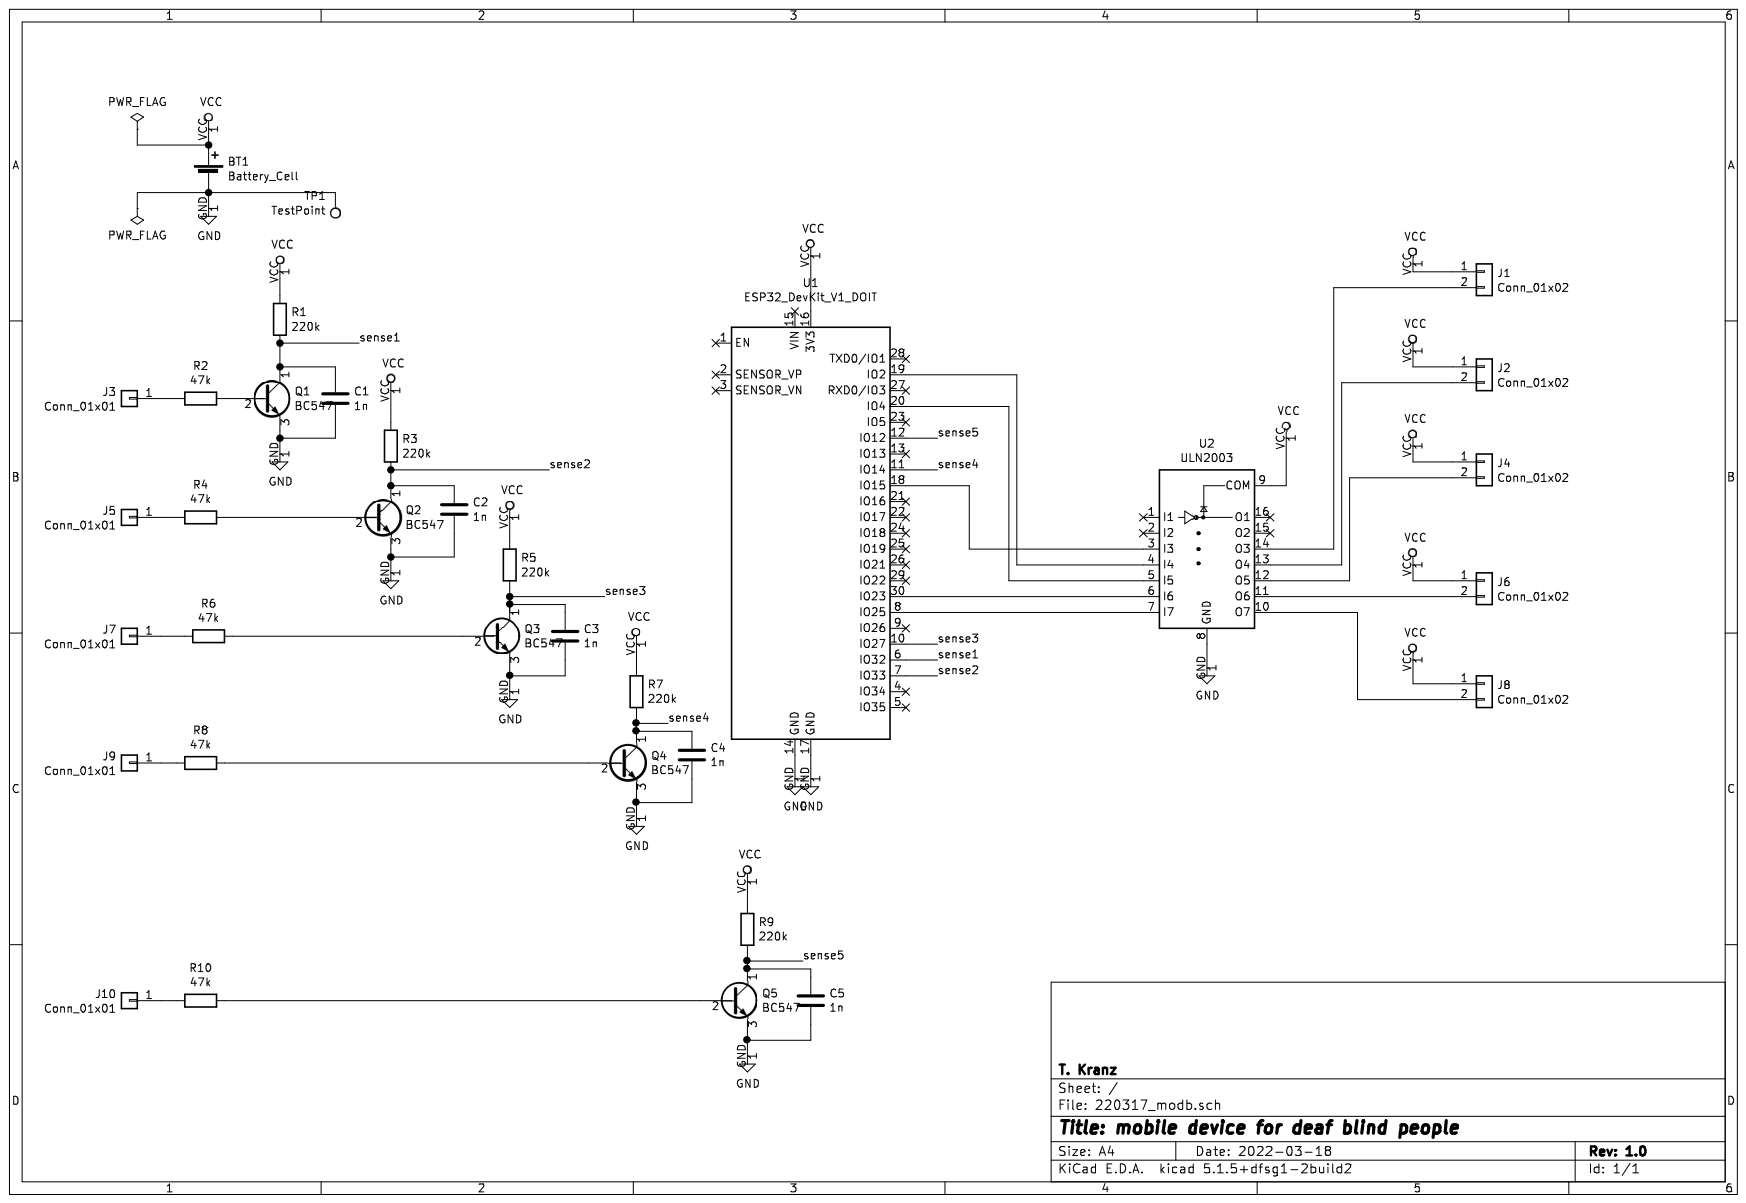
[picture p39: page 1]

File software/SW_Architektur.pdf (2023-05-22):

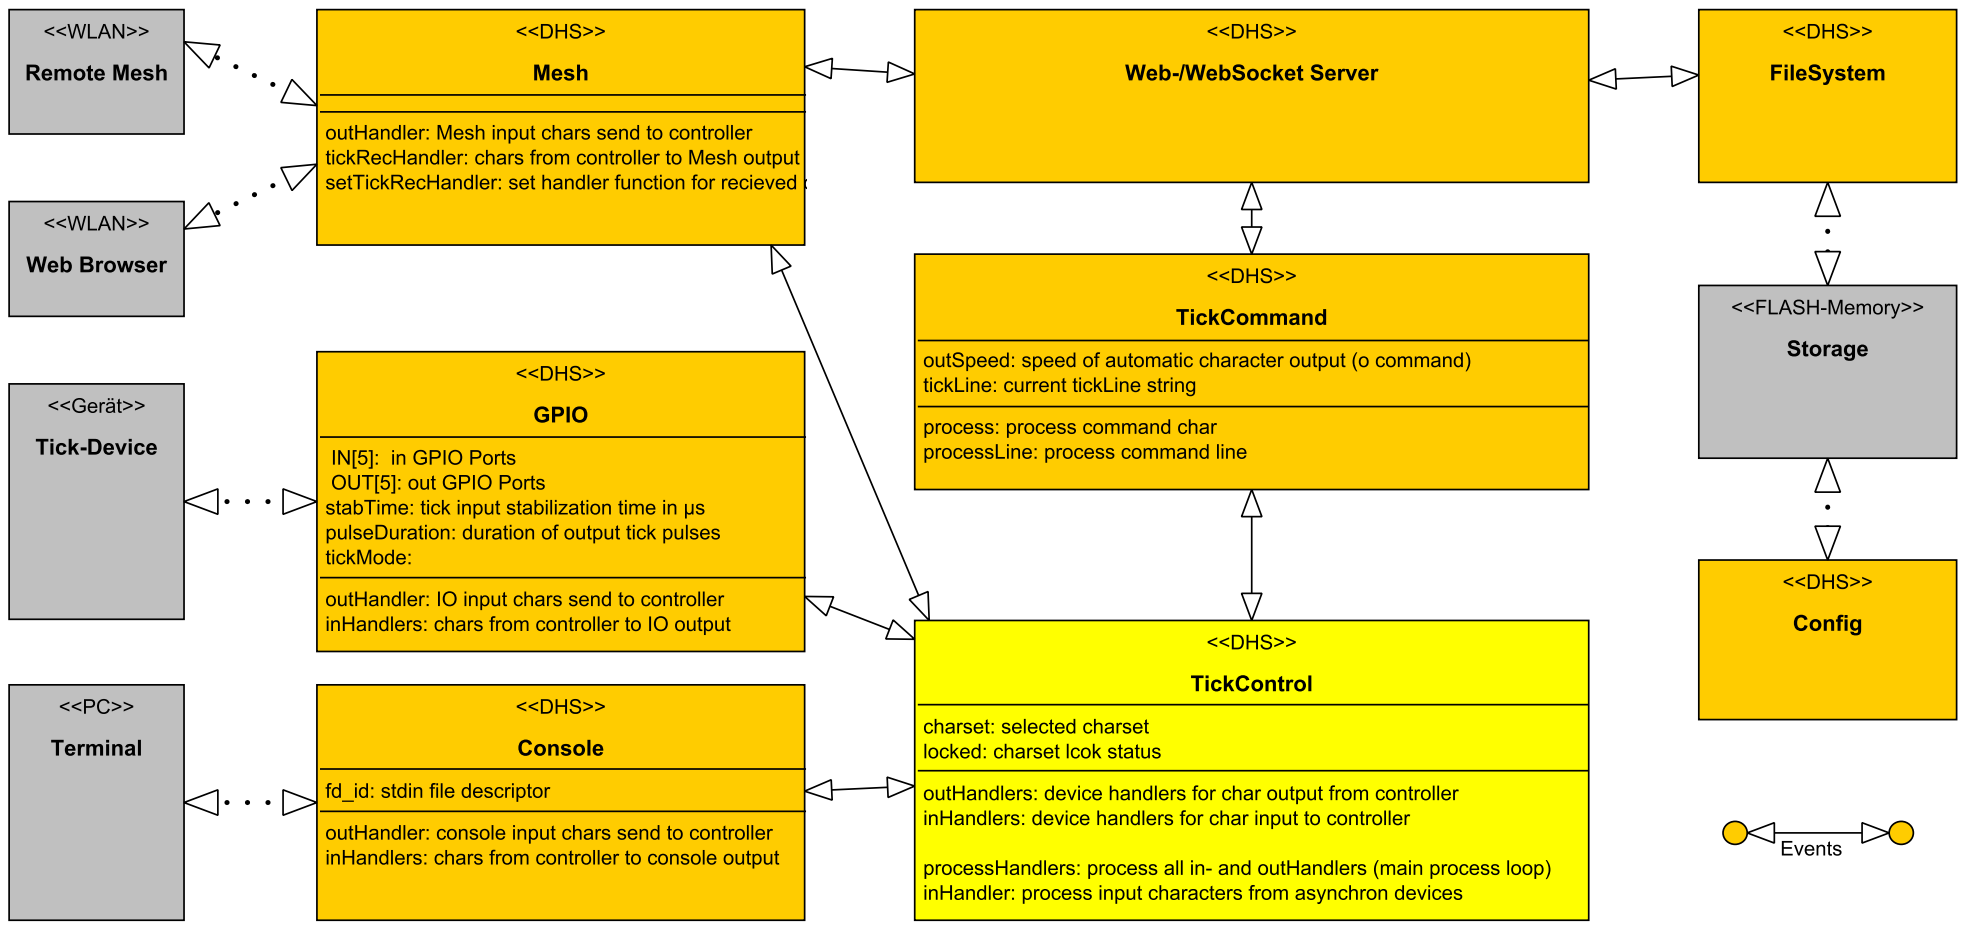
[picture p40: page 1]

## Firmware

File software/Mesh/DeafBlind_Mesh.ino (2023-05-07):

#include "DHSWiFi.h"          // own Network functions
#include "DHSWebsocket.h"     // own websocket functions
#include "tick.h"             // own tick processing functions

#define VERSION 0.17          // current SW-Version
// 0.05->0.06:  LED blink duration during WLan rooter search increased (+delay(10);)
//              Acces-Point channel = mesh channel
// 0.06->0.07:  autoreconnect(true) added to WiFi connection
//              WiFi Rooter search 40Sec.
//              WiFi.mode(WIFI_AP); WiFi.softAPConfig(myIP, myIP, IPAddress(255, 255, 255, 0)); for accespoint removed (disturbs mesh connection)
// 0.07->0.08   Added WiFi Scan function:to be continued, changed device name from dbserver to deafblind (same as mesh/access point name)
// 0.08->0.09   multi file download added
// 0.09->0.10   painless mesh-> after update comment all occurences of #ifdef ESP32 SPIFFS in ota.hpp to use LittleFS, otherwise initOTARecive will corrupt flash filesystem !!!
// 0.10->0.11   äöÄÖ changed to -+, problem with special characters in Websocket, to be corrected in newer version!
// 0.11->0.12   AccesPoint name changed to db (to avoid instable overlap with mesh network), added OLED ConnectType displ. W=WLAN, A=AccessPoint
// 0.11->0.14   Optimized AccessPoint/WLAN connection (hopefully)
// 0.14->0.16   Stability delay(1); added in painlessMeshSTA.cpp line 63 and 76 !!!, without crash scanComplete(): num = ... / several changes in painlessMesh lib, search for DHS comments...
// 0.16->0.17   Stability delay(1) removed, not neccessary with disabled scan, password removed (same password for mesh and access point neccessary)

#include <Wire.h>
#include <Adafruit_GFX.h>
#include <Adafruit_SSD1306.h>

#define SCREEN_WIDTH 128 // OLED width,  in pixels
#define SCREEN_HEIGHT 64 // OLED height, in pixels

#define I2C_SDA 33
#define I2C_SCL 35

// create an OLED display object connected to I2C
Adafruit_SSD1306 oled(SCREEN_WIDTH, SCREEN_HEIGHT, &Wire, -1);


Scheduler userScheduler;  // to control own task

String inputString = ""; // String to hold incoming data
tickC* tick;  // process tick class

void setup() {
  pinMode(LED, OUTPUT);  // on board LED defined in DHSWiFi.h
  digitalWrite(LED, 1);  // swith LED on during initialization
  Serial.begin(115200);  // init serial port

  Wire.setPins(I2C_SDA, I2C_SCL);
  Wire.begin(); 
  // initialize OLED display with I2C address 0x3C
  if (!oled.begin(SSD1306_SWITCHCAPVCC, 0x3C,false,false)) Serial.println("Failed to start SSD1306 OLED");

  oled.clearDisplay(); // clear display
  oled.setTextWrap(false);
  oled.setTextSize(2);         // set text size
  oled.setTextColor(WHITE,BLACK);    // set text color
  oled.setCursor(8, 0);       // set position to display
  oled.print("DB V"); // set text
  oled.print(VERSION);
  oled.setCursor(0, 16);       // set position to display
  oled.print(" Starting"); // set text
  oled.display();              // display on OLED
  Serial.println("Starting DeafBlind Device");

  delay(1000);  // wait for usb-port to initialize
  digitalWrite(LED, 0);  // swith LED off
  delay(1000);  // wait for usb-port to initialize
  digitalWrite(LED, 1);  // swith LED on
  delay(1000);  // wait for usb-port to initialize

  initWifi();       // start mesh network
  initServer();     // start web server
  startWebSocket(); // start WebSocket server
  tick = new tickC(); // initialize tick class

  inputString.reserve(200);
  
  Serial.printf("\nDHS V%4.2f  %s  %s  %s\n", VERSION, __DATE__ , __TIME__,__FILE__); // version / compile time information
        
  digitalWrite(LED, 0);  // swith LED off
  Serial.println("Deafblind Server running...");
}

int8_t xa=0,xe=0;
String text="";

void loop() {
  // get current time
  unsigned long now = millis(); 

  // process mesh communication
  WiFiLoop(); 

  // process webSocket messages
  webSocket.loop(); 

  // process command from serial port
  while (Serial.available()) { 
    char inChar = (char)Serial.read(); // get the new character:
    inputString += inChar; // add it to the inputString:
    if (inChar == '\n') { // if line complete
      if (inputString.length() > 4) tick->lineCommand(inputString.substring(0, inputString.length() - 2)); // if more than 1 character -> process line command without cr/lf
      else tick->processTick(inputString[0], 7); // process serial tick input
      inputString = ""; // clear line
    }
  }

  // process tick input
  if (char input = tick->getCharacter()) tick->processTick(input, 7);

  // check loop time for to high workload
  uint16_t calcTime = millis() - now;
  if (calcTime > 500) Serial.printf("Loop took %ld ms\n",calcTime);

  // repeat (100ns)
  usleep(100); 
}

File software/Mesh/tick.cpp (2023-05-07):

#include "tick.h"
#include <LittleFS.h>

#include <Adafruit_SSD1306.h>
#include "EEPROM.h"

#include "DHSWiFi.h"
#include "DHSWebsocket.h"

extern tickC* tick;
extern painlessMesh mesh;  // Mesh-Network class
extern uint8_t ConnectType;
extern uint8_t ConnectMesh;  // status of mesh connection

extern Adafruit_SSD1306 oled;

void tickC::loadSettings(char* FileN) {
  File f = LittleFS.open(FileN, "r");  // Open Setting file
  if (!f) {
    Serial.println(F("Error opening seting file for reading, use defaults"));
  } else {
    stabTime = atoi(f.readStringUntil('\n').c_str());
    Serial.printf("stabTime = %d\n", stabTime);
    outSpeed = atoi(f.readStringUntil('\n').c_str());
    Serial.printf("outSpeed = %d\n", outSpeed);
    pulseDuration = atoi(f.readStringUntil('\n').c_str());
    Serial.printf("pulseDuration = %d\n", pulseDuration);
    IN0 = atoi(f.readStringUntil(' ').c_str());
    IN1 = atoi(f.readStringUntil(' ').c_str());
    IN2 = atoi(f.readStringUntil(' ').c_str());
    IN3 = atoi(f.readStringUntil(' ').c_str());
    IN4 = atoi(f.readStringUntil(' ').c_str());
    OUT0 = atoi(f.readStringUntil(' ').c_str());
    OUT1 = atoi(f.readStringUntil(' ').c_str());
    OUT2 = atoi(f.readStringUntil(' ').c_str());
    OUT3 = atoi(f.readStringUntil(' ').c_str());
    OUT4 = atoi(f.readStringUntil('\n').c_str());

    Serial.printf("In0 %d In1 %d In2 %d In3 %d In4 %d  Out0 %d Out1 %d Out2 %d Out3 %d Out4 %d\n", IN0, IN1, IN2, IN3, IN4, OUT0, OUT1, OUT2, OUT3, OUT4);

    pinMode(OUT0, OUTPUT);  // init IO-Pins
    pinMode(OUT1, OUTPUT);
    pinMode(OUT2, OUTPUT);
    pinMode(OUT3, OUTPUT);
    pinMode(OUT4, OUTPUT);
#ifndef TOUCH
    pinMode(IN0, INPUT_PULLUP);
    pinMode(IN1, INPUT_PULLUP);
    pinMode(IN2, INPUT_PULLUP);
    pinMode(IN3, INPUT_PULLUP);
    pinMode(IN4, INPUT_PULLUP);

    previousinput = getIOs();  // init IO-State
#else
    previousinput = getTouch();  // init Touch-State
#endif
    String s = f.readStringUntil('\n');
    if (s != String("End\r")) Serial.println(F("Error reading seting file"));
    f.close();
  }
}

void tickC::saveSettings(char* FileN) {
  File f = LittleFS.open(FileN, "w");  // Open Setting file
  if (!f) {
    Serial.println(F("Error opening seting file for writing"));
  } else {
    f.println(stabTime);
    f.println(outSpeed);
    f.println(pulseDuration);
    f.printf("%02d %02d %02d %02d %02d %02d %02d %02d %02d %02d\n", IN0, IN1, IN2, IN3, IN4, OUT0, OUT1, OUT2, OUT3, OUT4);
    f.println("End");
    f.close();
  }
}

bool tickC::tickCallback(uint8_t num, char* payload) {  // websocket tick processing
  if (strlen(payload) > 2) tick->lineCommand(payload);  // if more than 1 character -> process line command
  else tick->processTick(payload[0], 7);                // process websocket tick input

  return false;  // continue processing for other callbacks
}

tickC::tickC() {

  pinMode(OUT0, OUTPUT);  // init IO-Pins
  pinMode(OUT1, OUTPUT);
  pinMode(OUT2, OUTPUT);
  pinMode(OUT3, OUTPUT);
  pinMode(OUT4, OUTPUT);
#ifndef TOUCH
  pinMode(IN0, INPUT_PULLUP);
  pinMode(IN1, INPUT_PULLUP);
  pinMode(IN2, INPUT_PULLUP);
  pinMode(IN3, INPUT_PULLUP);
  pinMode(IN4, INPUT_PULLUP);

  previousinput = getIOs();  // init IO-State
#else
  previousinput = getTouch();    // init Touch-State
#endif

  tickString.reserve(200);  // prereserve string space for faster execution
  tickLine.reserve(200);    // prereserve string space for faster execution

  pluginCallbacks[DHSNumPlugins] = tickCallback;  // set web socket callback for tick processing
  DHSNumPlugins++;

  tickClient = 1;                        // start as mesh client
  loadSettings((char*)"/ap.cfg");  // load current tick configuration
}

bool tickC::touchR(uint8_t Port) {
  int touchVal1, touchVal2, i = 0;

  touchVal1 = touchRead(Port);
  do {
    touchVal2 = touchRead(Port);
    i++;
  } while ((i < 5) && (abs(touchVal1 - touchVal2) > TOUCH_HYST));

  // Serial.printf("%d : %d\n",Port,touchVal2);

  if (touchVal2 < touchCompare) return true;
  else return false;
}

uint8_t tickC::getTouch() {  // get ticks from Touch-Device
  uint8_t input;
  // get inputs
  input = touchR(IN4);
  input = (input << 1) | touchR(IN3);
  input = (input << 1) | touchR(IN2);
  input = (input << 1) | touchR(IN1);
  input = (input << 1) | touchR(IN0);

  //Serial.printf("%d\n",input);
  return input;
}

uint8_t tickC::getIOs() {  // get ticks from IO-Device
  uint8_t input;
  // get inputs
  input = 1 - digitalRead(IN4);
  input = (input << 1) | (1 - digitalRead(IN3));
  input = (input << 1) | (1 - digitalRead(IN2));
  input = (input << 1) | (1 - digitalRead(IN1));
  input = (input << 1) | (1 - digitalRead(IN0));

  return input;
}


char tickC::getCharacter() {  // get input from IO-device

#ifndef TOUCH
  uint8_t input = getIOs();
#else
  uint8_t input = getTouch();
#endif

  if (input == previousinput) return (0);  // no finger change, dont wait

  if (input == 0) {  // all fingers up, dont wait
    previousinput = input;
    return (0);
  }

  if (tickMode & 1)
    if (input < previousinput) {  // only fingers removed, dont wait
      previousinput = input;
      return (0);
    }

  if (tickMode & 2) {      // old version (slower)
    unsigned long Millis;  // time
    previousinput = input;
    Millis = millis();

    do {  // wait for stable input
      delay(1);
#ifndef TOUCH
      input = getIOs();
#else
      input = getTouch();
#endif

      if (input != previousinput) {  // input changed?
        previousinput = input;       // reset input
        Millis = millis();           // reset timer
      }
    } while (millis() - Millis < stabTime);  // wait for input stabilization
  } else {
    delay(stabTime);  // wait stab time for all fingers to be placed

#ifndef TOUCH
    input = getIOs();  // read final input
#else
    input = getTouch();  // read final input
#endif

    previousinput = input;
  }

  if (input > 0) return tickChar[charSet][input];  // return tick character from current char set
  return 0;
}


void tickC::setCharacter(char c) {  // output character to IO-Device
  unsigned long currentMillis;
  unsigned long previousMillis = 0;  // last time
  int i;
  bool b0, b1, b2, b3, b4;

  for (i = 0; i < 32; i++)
    if (tickChar[charSet][i] == c) break;
  if (i == 32) {  // char not found
    Serial.print("?");
    return;
  }

  b0 = i & 1;
  b1 = i & 2;
  b2 = i & 4;
  b3 = i & 8;
  b4 = i & 16;

  uint8_t x = digitalRead(LED);
  if (x) digitalWrite(LED, 0);  // swith LED
  else digitalWrite(LED, 1);

  digitalWrite(OUT0, b0);  // pulse on
  digitalWrite(OUT1, b1);  // pulse on
  digitalWrite(OUT2, b2);  // pulse on
  digitalWrite(OUT3, b3);  // pulse on
  digitalWrite(OUT4, b4);  // pulse on
  previousMillis = millis();
  do {
    currentMillis = millis();
  } while (currentMillis - previousMillis < pulseDuration);  // wait interval time
  previousMillis = currentMillis;

  digitalWrite(OUT0, 0);  // pulse off
  digitalWrite(OUT1, 0);  // pulse off
  digitalWrite(OUT2, 0);  // pulse off
  digitalWrite(OUT3, 0);  // pulse off
  digitalWrite(OUT4, 0);  // pulse off

  digitalWrite(LED, x);
}


void tickC::lineCommand(String c) {  // process commands
  int pos;

  switch (c[0]) {  // process command
    case 's':
      stabTime = atoi((char*)&c[2]);
      Serial.printf("stabTime: %d\n", stabTime);
      break;
    case 'd':
      pulseDuration = atoi((char*)&c[2]);
      Serial.printf("pulseDuration: %d\n", pulseDuration);
      break;
    case 'x':
      outSpeed = atoi((char*)&c[2]);
      Serial.printf("outSpeed: %d\n", outSpeed);
      break;
    case 'o':
      for (int i = 2; i < c.length(); i++) {
        processTick(c[i], 7);
        delay(outSpeed);
      }
      break;  // output line on server only
    case 'r':
      sendWorld("Rebooting...\n", 4);
      ESP.restart();
      break;  // reset target
    case 'g':
      c[1] = '/';
      loadSettings((char*)&c[1]);
      break;  // load current configuration from file system
    case 'p':
      c[1] = '/';
      saveSettings((char*)&c[1]);
      Serial.printf("Config stored in %s\n", (char*)&c[1]);
      break;  // save current configuration in file system
    case 'c':
      pos = atoi((char*)&c[4]);  // set character in character set. Example: c ! 43
      if (pos / 32 < CHARSETNUM) {
        tickChar[pos / 32][pos % 32] = c[2];
        Serial.printf("Set %d, Pos %d: %c\n", pos / 32, pos % 32, c[2]);
      }
      break;
    case 't':
      tickMode = atoi((char*)&c[2]);
      Serial.printf(" tickMode: %d\n", tickMode);
      break;  // change tickMode
    case 'q':
      if (c.length() > 2) IN0 = atoi((char*)&c[2]);  // set IO-Ports Example q 15 04 18
      if (c.length() > 5) IN1 = atoi((char*)&c[5]);
      if (c.length() > 8) IN2 = atoi((char*)&c[8]);
      if (c.length() > 11) IN3 = atoi((char*)&c[11]);
      if (c.length() > 14) IN4 = atoi((char*)&c[14]);
      if (c.length() > 17) OUT0 = atoi((char*)&c[17]);
      if (c.length() > 20) OUT1 = atoi((char*)&c[20]);
      if (c.length() > 23) OUT2 = atoi((char*)&c[23]);
      if (c.length() > 26) OUT3 = atoi((char*)&c[26]);
      if (c.length() > 29) OUT4 = atoi((char*)&c[29]);
      pinMode(OUT0, OUTPUT);  // init IO-Pins
      pinMode(OUT1, OUTPUT);
      pinMode(OUT2, OUTPUT);
      pinMode(OUT3, OUTPUT);
      pinMode(OUT4, OUTPUT);
      pinMode(IN0, INPUT_PULLUP);
      pinMode(IN1, INPUT_PULLUP);
      pinMode(IN2, INPUT_PULLUP);
      pinMode(IN3, INPUT_PULLUP);
      pinMode(IN4, INPUT_PULLUP);
      previousinput = getIOs();  // init IO-State
      Serial.printf("In0 %2d In1 %2d In2 %2d In3 %2d In4 %2d  Out0 %2d Out1 %2d Out2 %2d Out3 %2d Out4 %2d\n", IN0, IN1, IN2, IN3, IN4, OUT0, OUT1, OUT2, OUT3, OUT4);
      break;
    case 'w': // change WiFi channel
      strlcpy(channel,(char*)&c[2],32);
      Serial.printf(" Cahnnel: %s\n", channel);
      if (!EEPROM.begin(256)) {// size in uint8_t
        Serial.println("Failed to initialise EEPROM");
      }
      else {
        EEPROM.writeULong(0,123456789);
        EEPROM.writeString(4, ssid);
        EEPROM.writeString(4+32, password);
        EEPROM.writeString(4+32+32, channel);
        EEPROM.end();
      }
      sendWorld("Rebooting...\n", 4);
      ESP.restart();
      break;  // change tickMode
  }
}
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

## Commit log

2022-03-08 Add Arduino sketch
2022-03-17 Add files via upload
    Handscan of the play dough model which Bernd created as a first prototype of a handheld device
2022-03-19 Add files via upload
    Bild der Platine mit erstem Placement
2022-04-12 parameter changes for project. Marked with 220306 Kr
    static uint16_t __touchMeasureCycles = 0x2000; was originally 0x1000
    /* 220306 Kr change according to recommendation */
    /* clear bits for DRANGE before setting new value*/
    CLEAR_PERI_REG_MASK(RTC_IO_TOUCH_CFG_REG, RTC_IO_TOUCH_DRANGE_M);
    /* set value to 01 = 1V range */
    SET_PERI_REG_BITS(RTC_IO_TOUCH_CFG_REG, RTC_IO_TOUCH_DRANGE, 1, RTC_IO_TOUCH_DRANGE_S);
2022-08-27 Gedanken von Bernd
    [2xFiPS direkt Varianten A+B.xlsx]
2023-04-14 Add files via upload
    several prototypes
2023-05-07 Used Libraries
    Unzip into Arduino-IDE libraries folder...
